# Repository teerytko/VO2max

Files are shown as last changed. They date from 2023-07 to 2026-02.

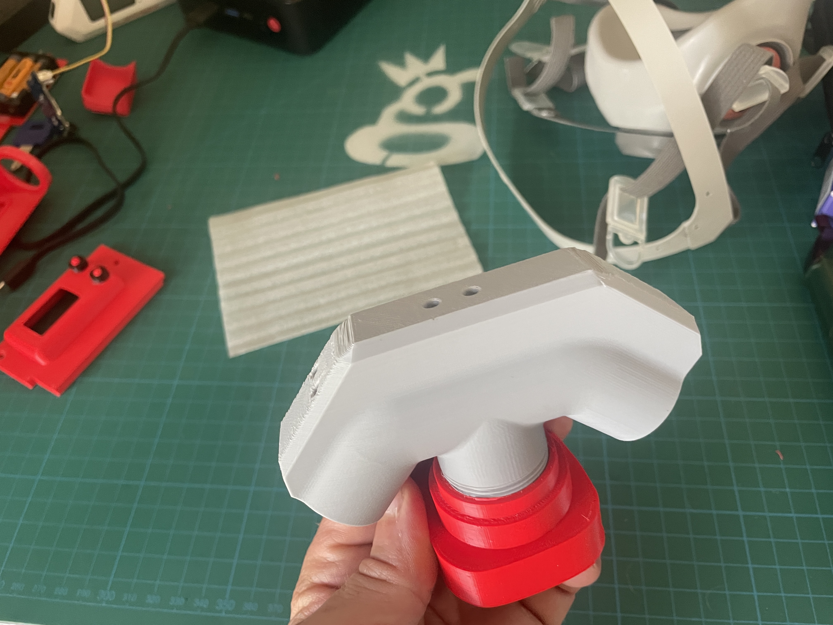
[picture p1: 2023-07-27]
images/first_print_v4_test.jpg

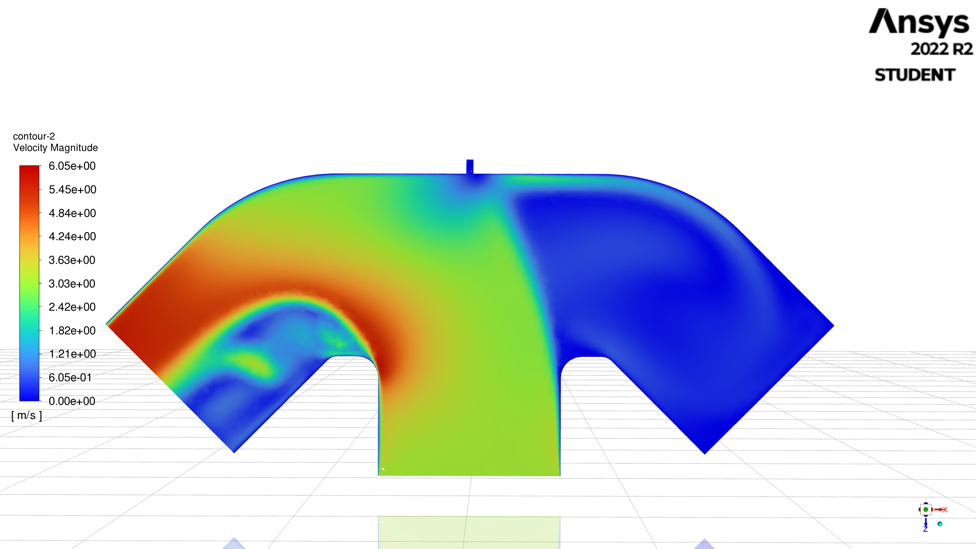
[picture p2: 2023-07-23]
images/flipped_CFD_results_w_velocity_contours.png

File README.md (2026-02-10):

# VO2 Max Mask 
Super cool project to build your own VO2 Max mask.  Your "VO2 Max" is a measure of how much oxygen your body and absorb and use during exercise, read more about it [here](https://www.healthline.com/health/vo2-max#benefits).

Original idea and detailed build instructions can be found on [Instructable](https://www.instructables.com/Accurate-VO2-Max-for-Zwift-and-Strava/). Other designs can be found [here, a UC Davis Med Center project](https://faculty.engineering.ucdavis.edu/knoesen/wp-content/uploads/sites/119/2016/12/OOCOO_WirelessHealthSubmission_Final.pdf) and a [commercial version that costs just under US$6,000](https://vo2master.com/).

This fork of [excellent Github work](https://github.com/meteoscientific/VO2max) incorporates the CO2 enhancements. The intent with this repo is to make it as easy as possible to build a world class piece of kit that'll add useful metrics to your training.

## Design Constraints
Less than $200 for all parts and printing.
Printable by anyone with a 3D printer (easy print files).
Can handle up to 200 liters per minute of exhaled air.
Small and light enough to be worn for a full workout.
Able to measure resting as well maximum VO2.

## App Intent
Allows an athlete to monitor real time [RER](https://www.adinstruments.com/signal/rer#:~:text=Respiratory%20Exchange%20Ratio%20(RER)%20is,is%20operating%20aerobically%20or%20anaerobically.).

Allows an athlete to monitor gross mechanical efficiency

The main mini version now aims to do just the basic VO2, VCO2 measurements, which can be sent via BLE to external device (e.g. phone). Any other sensors should connected to the phone as a data collection device.

## Versions
- V1 - Original version that works, can be found via the Instructable link above.
- V2 - Upgraded version by Urissel & Ivor, includes the CO2 & ambient temp/pressure to adapt to different elevation & temperatures.
- V3 - Proposed by Mahmoud, this is the T version.  Currently abandoned due to issues with getting correct sensor readings.
- V4 - Proposed by Stefan, affectionately called "The Snork".  Latest version.
- V5 - My latest version is based of V1, but not yet finalized. 

## Recent Firmware Status (as of 2026-02-08)
Latest commits in this repo:
- `f149ecc` (2026-02-08): Update the JSON outputs and scripts to match.
- `c29ee34` (2026-02-07): Add support for scripts parsing serial outputs.
- `f1a9a76` (2026-02-07): Refactor VO2 BLE server and serial output.
- `85bd076` (2026-02-07): Split BLE data into separate characteristics.
- `75d0030` (2026-01-06): Refactor volume calculations.

The active PlatformIO firmware lives in `TTGO_PlatformIo` and includes:
- `src/main.cpp`: Full firmware variant.
- `src/main_mini.cpp`: Newer "mini" variant with JSON serial telemetry and BLE service split.
- `src/vo2_ble_service.h` and `src/vo2_ble_service.cpp`: BLE server wrapper with separate characteristics for VO2, VCO2, and RQ.
- `tools/`: Python utilities for parsing and plotting serial JSON output.

### Steps to Build & Use
Check the build notes in `TTGO_PlatformIo/README`.

## Order Sensors, board, and assorted fasteners.
Check the [BOM](https://github.com/meteoscientific/VO2max/blob/main/BOM.md) for all the various parts to order, they can take a week or two to come in.

## Print 3D Parts
Print out the 3D parts using PLA.  This is still a work in progress, but feel free to explore the 3D Test Print directory and print out what you'd like.  Nothing works well yet (Aug 4th, 2023).

<br>Test fit all parts and make sure you know where everything goes; that will make the next steps much easier.

## Program Board
Originally this project was built with the Arduino IDE.  A few of us nerds decided that Platformio might be easier and more rad, so we're using that.

When you first get the board, hold down the boot button while plugging it in, and keep that down.  You need to erase everything on the board before you load the rest.  From there, you should be able to use the Platformio folder to load everything you'll need.  I did this on a Windows computer (a little Beelink with a monitor & display) because I couldn't get it to work on my Mac.

Current PlatformIO commands (from `TTGO_PlatformIo`):

```bash
platformio.exe run -e lilygo-vo2mini
platformio.exe run --target upload -e lilygo-vo2mini
platformio.exe test -e lilygo-vo2mini
platformio.exe device monitor -e lilygo-vo2mini
```

## Serial Output Tooling (JSON)
The `TTGO_PlatformIo/tools` directory now contains utilities for processing JSON serial output from the firmware:
- `serial_file_parser.py`: Parse JSON-lines from serial (`--port`) or from a captured file (`--file`).
- `live_visualize_serial.py`: Live plot JSON events from a serial port.
- `visualize_output.py`: Aggregate captured JSON-lines and generate HTML/PNG plots.

Install requirements and run examples:

```bash
python -m pip install -r TTGO_PlatformIo/tools/requirements.txt
python TTGO_PlatformIo/tools/serial_file_parser.py --port COM6 --baud 115200 --out-file output.json
python TTGO_PlatformIo/tools/visualize_output.py --input output.json --out-html output_plots.html --out-dir output_plots
```

## Wire It Up

## Assembly

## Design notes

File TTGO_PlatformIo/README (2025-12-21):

# Lilygo-T-Display VO2Max

# build (cmd line)
platformio.exe run -e lilygo-vo2mini

# build and upload (cmd line)
platformio.exe run --target upload -e lilygo-vo2mini

# test
platformio.exe test -e lilygo-vo2mini

# monitor / debug prints
platformio.exe device monitor -e lilygo-vo2mini

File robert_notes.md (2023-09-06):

Robert found this project and had the following notes, all relevant to the v1 form factor (not the v4 "Snork" designed by Stefan).

## Oxygen sensor:
1. As we know there is (or was) the issue of condensing air. In the new design it shouldn't be an issue anymore, if I'm correct? 
Anyway, I don't know which sensors the expensive spirometers use (do you?), but I'm guessing it's an oxygen sensor from the medical field.

Here's a [list of City Techs/Honeywell oxygen sensors](https://euro-gasman.com/app/uploads/2020/11/CITY-TECH-OXYGEN-SENSORS-LIST.pdf). Take a closer look at the "MediceL" ones: they are typically used for medical applications. 

The "best" as in "fastest response time" is the [MOX20](https://euro-gasman.com/app/uploads/2020/11/O2-MOX-20-MEDICEL-V2.pdf). It has a response time of <0.75s. That's quite fast, isn't it? If I remember correctly the data shouldn't be polled more often than once per second. Of course, being the fastest sensor comes at a high price (>$200).

What I noticed is that none of these sensors should be operated in condesing air. Even the MOX20 also states "Operating Humidity Range: 0-99% RH non-condensing". I haven't found a suitable sensor (T90 <5s) which works in a condensing environment. This leads me to believe that this can only be solved by design meaning we need to have a design which reduces condensate to a minimum.

Expensive spirometers will most likely use a sensor which won't work well in condensing air.

2. Response time: What is the response time of sensors used in expensive spirometers? I'm honestly guessing they are slower than 5s. Probably in the range of 5-15s. Which really is not that much of an issue for most of the time and as we are building a similar device we need to think about the importance of a fast response time. A faster than usual response time may even produce higher VO2max values than what the athlete might expect (I'll share more about that in the section "Calculations").

3. What I think we need is a cheap, fast enough, very reliable and if possible as long lasting oxygen sensor as possible. These sensors have pretty much an expiration date from the moment you first get them. Using a sensor with a high stability should be preferred.

4. I don't have a recommendation yet as I haven't really tested my VO2max mask enough. I read that some people complain about wrong readings, but I can't confirm that. If it works well the sensor should be suitable.

## CO2 sensor:
1. The SCD30's measurement range is not suited for accurately measuring our exhaled CO2 concentration. The range is 0-40,000 ppm which equals 0-4 vol%. As far as I know the exhaled CO2 concentration is always around the 4% mark (and my own tests confirm that). This makes the sensor inaccurate. 

2. Response time: The SCD30 has a pretty high response time of 20s to τ63%. Contrary to what I first thought this might not be that much of an issue, because we really only need CO2 for aerobic work measurements meaning at a VO2 below the maximum (depends on the athlete and the range should be from 60% VO2max to up to 90%). The reason is that the RQ should be at or higher than 1.0 as soon as the fat oxidation stops. This typically happens at your MaxLaSS (maximum lactate steady state, which is not the same but similiar to the FTP in biking). Below that threshold it doesn't really matter if it takes a minute to output the correct value, except for in-depth training analysis of high intensity workouts.

3. Keeping that in mind I'd say that having a low response time (<10s) is just an optional feature. Of course it shouldn't take much longer than the current SCD30 is able to accurately determine the CO2 concentration. The plus side is that CO2 sensors don't really come with an expiry date or it's as high as >10 years, so that's of no concern for us.

4. Recommendation? Well, again that's hard. I've searched but haven't really found the most suitable sensor for our device. There are some automotive sensors but I honestly forgot why I thought they aren't a good fit. Another sensor from Sensirion that uses a completely different technology than NDIR (SCD30) is the STC31, which uses a thermal conductivity measurement principle. Let me tell you the advantages first: it can measure a CO2 concentration of 0-25 vol% (or 0-250,000 ppm).

We'd only really need 0-5 vol%, but that's okay. It has an extremely fast measurement time of 66 ms, although I don't know how that value compares to the SCD30 as it says "measurement time" and not "τ63%". It works up to a humidity of 40°C dew point and does not seem to have issues with condensing air (the SCD30 does!). 40°C dew point is just a bit more than we need. It's extremely small. However, on the downside the accuracy of 0.5 vol% + 3% measured value might be too low and the small form factor makes it pretty much impossible to solder manually, but there are options available.
What do you think?

## Pressure sensor:
I haven't taken a look at this sensor. But I always wondered why we don't use something like the Sensirion SFM3400-AW (https://www.mouser.com/datasheet/2/682/Sensirion_Datasheet_SFM3400_AW_SFM3400_D-3002584.pdf)? Is it the price? This would eliminate the need to calibrate the sensor with a 3l calibration syringe.

## Ambient pressure sensor:
The current one seems to be okay, although the first one I got didn't work. Maybe my soldering skills were that bad and destroyed it but I think Nik (or someone else) had the same problem. Sounds to me that they aren't that reliable?

## Air flow:
The original design definitely had issues due to outside airflow interfering with the measurements. Think about this: When you are doing a VO2max test you will most likely run a fan or an ac. The fan will push air exactly in the direction the mask is facing. During my tests without a fan I could see changes in the measured expiratory volume and ventilation frequency just by moving around a little. Using a fan or an ac completely made the results unreliable. 

The new design will most likely be less affected by this, but even then the CO2 sensor might produce wrong results as the CO2 concentration will drop by a lot. This will probably not happen during VO2max tests (remember CO2 is not really of concern when measuring the VO2max) due to high ventilation, but it can happen when you want to know the correct CO2 concentration which is when you are working aerobically.
So what I did is inserting a 3M exhalation valve (exactly the same blue one which is included in the 3M mask) in the front of the original design. This is a single part I just glued on for testing purposes.

## Calculations:
1. I honestly haven't checked each calculation but I'm relying on them to be accurate.  What I noticed is that the VO2max might be a bit too high. When I did my last test with an expensive spirometer the guy said that sometimes a "single breath can produce a higher VO2" which is why he doesn't use this value to determine the VO2max and instead uses the highest average of 30s or something like that. This should be checked.

2. The CO2 sensor accepts ambient pressure readings. I have implemented that in my version of the code as we have the BMP280 to provide that data.

## Code:
1. I have replaced the existing SCD30 library with another one as the CO2 sensor needs to be calibrated from time to time (and due to the pressure sensor addition). We are not using the automatic self calibration which normally should be used with SCD30. This automatic calibration assumes that in a given time the sensor will reach the atmospheric CO2 concentration at least once. Automatic self calibration takes at least many hours up to days, which is not suitable for our device. Instead I implemented a function to self calibrate the CO2 sensor by running it for at least 2 minutes in outside air. Then it'll calibrate to 421 ppm which is the current atmospheric CO2 concentration of 2023. Remember, due to increasing CO2 in the air the value will increase each year and therefore using a value of 400 ppm would already create an error of 5% during calibration (not something we want in an accurate device). 2 minutes might not be enough but this step can be repeated or I can increase the timer in the code.

2. For my own tests I've changed some of the BLE code. In the future I would like to output all useful data to an app similar to a bike computer. The implementation can be done on the bluetooth level by sending each value as a specific service. This can then be combined with powermeter data, heart rate data and so on and even be saved in a FIT file or something like that.

There is an amazing website for analyzing of these files (www.intervals.icu) and the developer is a great guy who always listens to new ideas and often implements them (quite quick actually!).
The app itself is a work in progress and just something I would use but I can share it if it'll ever be ready.

5. The user interface could use an overhaul. My idea is to create multiple sections on the initial screen to make it more clear (Start, Settings, Status) and by using submenus to navigate further.

6. The code has quite a lot of comments (thanks for that) which make it easy to understand. Still it could be reorganized a little. But that's not really important now.

I've probably forgot some points but I'll share them if I remember.
Let me know your thoughts.

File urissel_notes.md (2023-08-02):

*I found the notes from Ulli Rissel in Rabbitcreek's updates hard to read as one giant paragraph, so I've broken them down a bit here, cut some parts out that related to the original venture tube design, and added in a few of Ulli's notes.*

## Upgrades from original:

  1. I added a barometric sensor (BMP180) to calculate the air density. The calculation of VO2 should also be correct in the mountains thanks to the barometric sensor. The BMP180 sensor is connected to the I2C bus like the other sensors. I glued it between the two sensors on the Venturi tube. In Arduino, the library "Adafruit_BMP085" must be added.

  2. The VO2max and VEmin calculation is carried out with moving averages and measurement of each individual breath. This allows current measured values every 5 seconds. 

  3. The displays of the values can be switched during the measurement.

  4. If the sensor reaches its limit (at approx. 4.5L/s corresponding to a VEmin of 136L/min!) this is displayed. However, the error should only be minimal. If the limit is displayed too often, the Venturi nozzle would have to be modified. 

  5. A warning appears if the O2 sensor measures less than 20% VO2% at startup. Then the sensor (or room) needs to be ventilated before moving on. If "Continue" is pressed anyway, the value is set to 20.9%.

  6. Battery indicator: The voltage is displayed with background color to the state of charge. White: USB or charge, Green: Battery full, Yellow: Battery approx. 50%, Red: Battery approx. 20%. The display takes place at the top left. A 1100mAh Lipo lasts about 10h!

  7. Kcal are now calculated correctly with their own integral timer.

  8. DEMO mode when the top button is pressed when powered on. It simulates about 28L of respiratory minute volume with respiratory rate of 12 at 4% CO2. This allows you to test the data transfer.

  9. Reset by pressing both buttons. This works after the 3L check.

  10. The volume measurement was measured with a 3L calibration pump and a calibration factor was programmed. The volume measurement can be checked in the first 10 seconds with a real-time display. I tested 2 sensors and for practical reasons set the average calibration factor 0.92 for volume measurement. 

You are welcome to customize this in the program itself (is easy to find).

  11. The data is sent every 5 seconds as csv via USB cable and Bluetooth serial. Data transmission with cable and BT starts immediately after "Press to start". With Excel Datastream, a display can be made in real time.BT on Excel works really well, even with instant graphical representation. 

You can also send the data to the APP Bluetooth Serial Monitor on an Android mobile phone and process or send it from there.

### Some thoughts on the calculation: 

The common spirometers measure the inspiration volume Vi in the supply line, not Ve. 

However, the concentration of O2 and CO2 is measured **expiratory**. 

Therefore, Ve must be calculated in order to correctly record the O2 consumption. 

Three factors come into play: 
  1) The volume shrinks minimally if less CO2 is produced than O2 is absorbed (i.e. at quotient <1). This can be corrected via the Haldane formula. However, the deviations are minimal. 
  2) Much more important is that BTPS conditions prevail in the expiration air (35°C, 95% humidity, actual ambient pressure). 
  3) The measurement has to be converted to STPD conditions (0 °C, 1013.25 hPa, 0% humidity). 

VO2 is defined under STPD conditions. STPD stands for standard temperature (0°C or 273 K) and pressure (760 mm Hg) and dry (no water vapor). 

According to my research, the conversion is nothing more than the ratio of the density of BTPS (actually measured pressure, 37°C, 95% humidity) to STPD. 

*The two symbols BTPS and STPD represent two conventional conditions used when discussing respiratory gases. BTPS stands for body temperature (37°C), ambient pressure and gas saturated with water vapor, whereas STPD stands for standard temperature (0°C or 273 K) and pressure (760 mm Hg) and dry (no water vapor). Pulmonary ventilation (1/min) is usually measured at BTPS, whereas gas volumes in blood are usually expressed at STPD. To convert a gas volume at BTPS to one at STPD, one needs to multiply the former volume by (273/310) (PB − 47) / 760.* [National Library of Medicine reference](https://www.ncbi.nlm.nih.gov/books/NBK54114/)

The density of STPD is constant = 1.2922 kg/m³. The density of BTPS can be easily calculated, whereby instead of the gas constant 287.058, the constant for moist air is used for BTPS (about 292.8). 

The constant fluctuates in our temperature range depending on pressure only by a few percent, the density only in the per mille range, if 292.8 is not adjusted. The density indicates how many molecules are in the air.  And now it becomes relatively simple: We measure Ve directly, so no further conversion is required. 

This results in: VO2 = Ve * O2diff% * Density BTPS / 1.2922. Done! By the way, according to the spirometry instructions, VO2 is only calculated from the O2 difference. 

The density must be related to the density under standard conditions. This means that rho must be divided by 1,225. All values are then about 20% lower:

co2 = initialO2 - lastO2; //calculated level of CO2 based on Oxygen level loss
if (co2 < 0) co2 = 0; // correction for sensor drift
vo2Total = volumeVEmean * (rho/1.225) * co2 * 10; // = vo2 in ml/min (* co2% * 10 for L in ml)
vo2Max = vo2Total / weightkg; //correction for wt

VO2Total and vo2Max in ml/min/kg
volumeVEmean: breath volume in L/min. (running mean)
rho: density of the air in kg/m³

CO2 is only used to calculate the quotient and for the Haldane formula, which we do not need.

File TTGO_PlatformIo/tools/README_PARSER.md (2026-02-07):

Serial/File Parser

This repository includes a small Python utility that reads lines from either a text file or a serial port and prints parsed output.

Files:
- [scripts/serial_file_parser.py](scripts/serial_file_parser.py)
- [requirements.txt](requirements.txt)

Install dependencies:

```bash
python -m pip install -r requirements.txt
```

Examples:

Read a file:

```bash
python scripts/serial_file_parser.py --file data.txt
```

Read from a serial port (Windows example):

```bash
python scripts/serial_file_parser.py --port COM6 --baud 115200
```

Options:
- `--raw`: print raw lines (or JSON records if lines are JSON)
- `--limit N`: stop after N lines

Behavior:
- Each input line is first attempted to be parsed as JSON; if parsing fails the line is returned as raw text.

Visualization:

- A visualization utility is available at `scripts/visualize_output.py` that reads a JSON-lines file (like `output.json`), aggregates measurements per "expiration" event and creates interactive and static plots.

Examples:

```bash
python scripts/visualize_output.py --input output.json --out-html output_plots.html --out-dir output_plots
```

This will create `output_plots.html` (interactive Plotly charts) and PNG files in the `output_plots` directory.

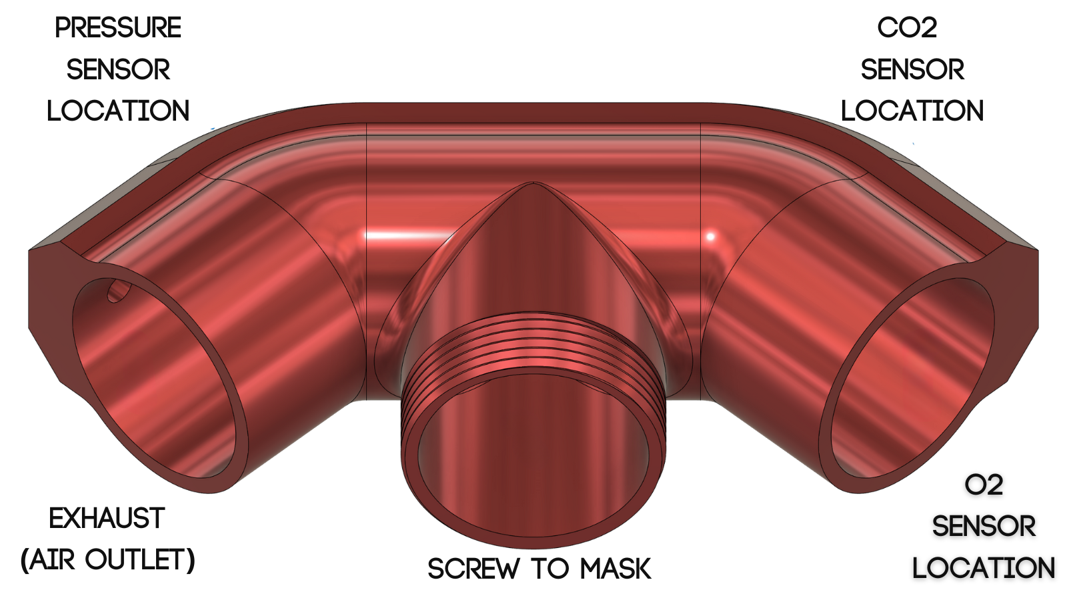
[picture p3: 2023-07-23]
images/redesign_of_VO2_Max_housing.png

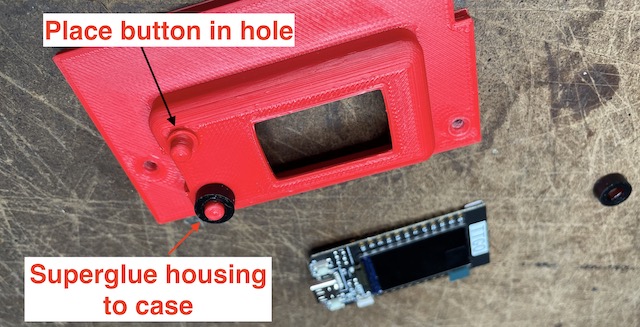
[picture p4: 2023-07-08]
images/button_housing.jpg

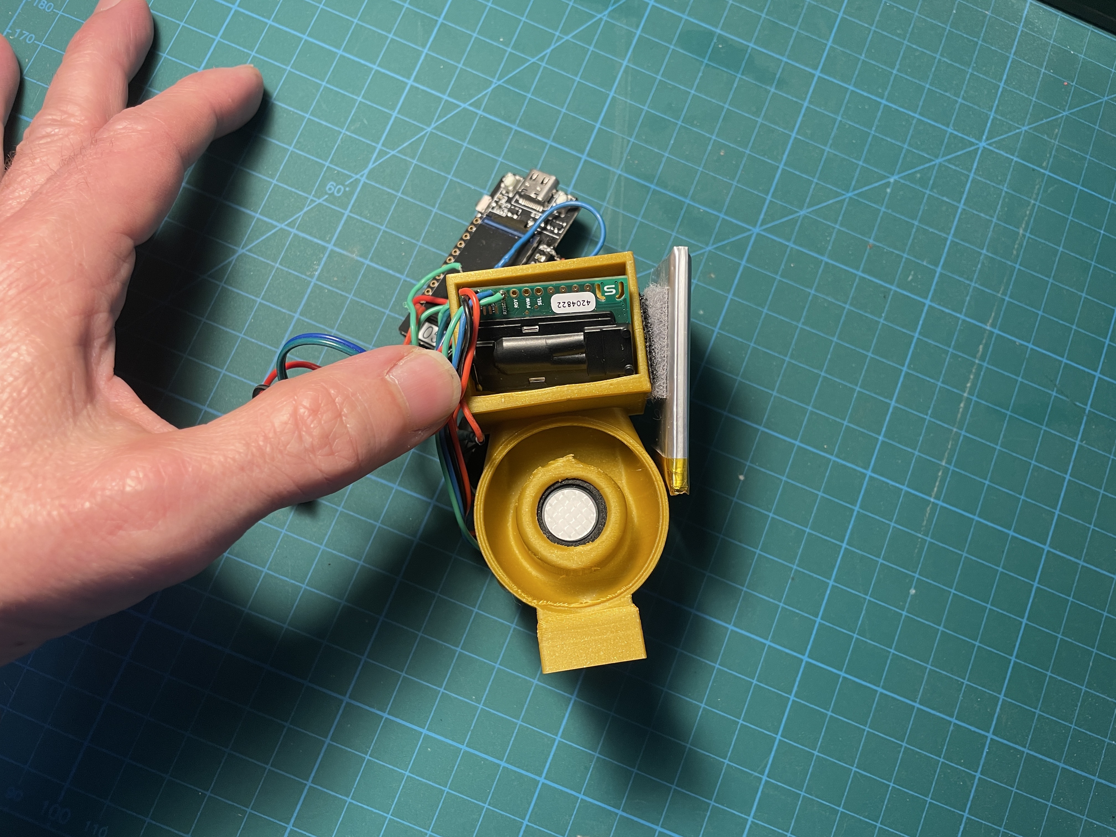
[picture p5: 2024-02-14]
images/v4_snork/vo2_inside.JPG

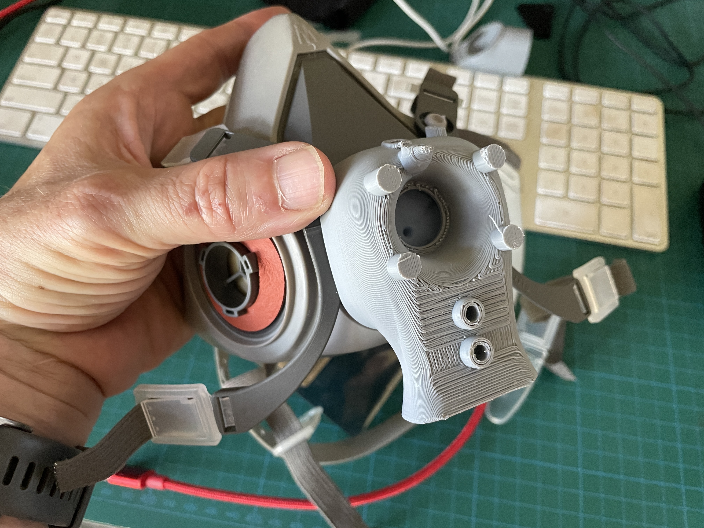
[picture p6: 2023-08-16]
images/v4_snork/v4_snork_1.jpg

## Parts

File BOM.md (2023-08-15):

## Bill of Materials

### USA

| Item | Description/Details | Source | Est Cost |
| --- | --- | --- | --- |
| board (the brain) | ESP32 T-Display, 16MB CH9102F | [Amazon](https://www.amazon.com/gp/product/B099MPFJ9M/) | $19 |
| battery| Lipo Battery, 1000 Mah, E503450 3.7v |  [Amazon](https://www.amazon.com/gp/product/B07BTV3W87/ref=ox_sc_act_title_1?smid=A132D7PL1YID8X&psc=1) | $12 |
| pressure sensor | BMP280, calculate air density |  [Amazon](https://www.amazon.com/gp/product/B01ICN5QPU/ref=ox_sc_act_title_1?smid=A30QSGOJR8LMXA&psc=1) | $6 |
| screws | 2 x M3 x 8mm | [Amazon](https://www.amazon.com/Hilitchi-510-Pcs-Button-Socket-Assortment/dp/B073SWNV5N/) | $15 for kit |
| threaded inserts (original design only) | M3 x 8 x 5mm | [Amazon](https://www.amazon.com/gp/product/B096MD67WB/) | $18 for kit |
| aquarium tubing (original design only) | standard 3/16", 4mm inside diameter (ID) |  [Amazon](https://www.amazon.com/AQUANEAT-Standard-Airline-Aquarium-PREMIUM/dp/B01N8SNNOI/) | $6 |
| o-ring | for oxygen sensor, 22x19x1.5mm | [Amazon](https://www.amazon.com/uxcell-Silicone-Rings-Diameter-Gasket/dp/B082STZ4XL?th=1) | $7 for 30 |
| jumper wire | for making board-sensor connections | [Amazon](https://www.amazon.com/TUOFENG-Hookup-Wires-6-Different-Colored/dp/B07TX6BX47?th=1) | $15 |
| oxygen sensor | Gravity: I2C Oxygen Sensor |  [DF Robot](https://www.dfrobot.com/product-2052.html) | $75 |
| differential pressure sensor | Omron--D6F-PH0025AD2 |  [Digikey](https://www.digikey.com/en/products/detail/omron-electronics-inc-emc-div/d6f-ph0025amd2/15197363) | $28 |
| cable for diff press sensor | DF-CABLE3 |  [Digikey](https://www.digikey.com/en/products/detail/omron-electronics-inc-emc-div/D6F-CABLE3/9471785) | $12 |
| mask | half mask, particulate matter, 6200/07025 | [Digikey](https://www.digikey.com/en/products/detail/3m/6200-07025/7693860) | $22 |
| CO2 sensor | SCD30 |  [Digikey](https://www.digikey.com/en/products/detail/sensirion-ag/SCD30/8445334) | $62 |
| on/off switch | mini push button |  [Adafruit](https://www.adafruit.com/product/1683)| $6 |

### EU

| Item | Description/Details | Source | Est Cost (€) |
| --- | --- | --- | --- |
| board (the brain) | ESP32 T-Display, 16MB CH9102F | [Amazon](https://www.amazon.de/-/en/gp/product/B099MPFJ9M) | €23 |
| battery| Lipo Battery, 1000 Mah, E503450 3.7v |  [Amazon](https://www.amazon.de/-/en/gp/product/B09GK98KZK) | €18 |
| pressure sensor | BMP280, calculate air density |  [Amazon](https://www.amazon.de/-/en/gp/product/B0BN1NXG4D) | €6 for 5 |
| screws | 2 x M3 x 8mm | [Amazon](https://www.amazon.de/-/en/340pcs-Stainless-Screws-Button-Assortment/dp/B08H24T1DJ) | €9 for kit |
| threaded inserts (original design only) | M3 x 8 x 5mm | [Amazon](amazon.de/gp/product/B09ZHSGHXD) | tbd |
| aquarium tubing (original design only) | standard 3/16", 4mm inside diameter (ID) | [eBay](http://ebay.de/itm/183220505584?var=691579886173) | tbd |
| o-ring | for oxygen sensor, 22x19x1.5mm | [Amazon](https://www.amazon.de/-/en/gp/product/B00AKW4MM0) | €5 for 10 |
| jumper wire | for making board-sensor connections | [eBay1](ebay.de/itm/184844268251) [eBay2](ebay.de/itm/184844268251) | tbd |
| oxygen sensor | Gravity: I2C Oxygen Sensor |  [Mouser](https://eu.mouser.com/ProductDetail/426-SEN0322) | €49 |
| differential pressure sensor | Omron--D6F-PH0025AD2 |  [Mouser](https://eu.mouser.com/ProductDetail/653-D6F-PH0025AD2) | €26 |
| cable for diff press sensor | DF-CABLE3 |  tbd | tbd |
| mask | half mask, particulate matter, 6200/07025 | [Amazon](https://www.amazon.de/-/en/gp/product/B005HK05L2) | €21 |
| CO2 sensor | SCD30 |  [Amazon](https://www.amazon.de/-/en/gp/product/B0B9MYCL3S) or [Watterott](http://shop.watterott.com/Sensirion-SCD30-CO2-Kohlendioxid-Sensor) | €43 |
| on/off switch | mini push button |  [Mouser](https://eu.mouser.com/ProductDetail/Adafruit/1683)| €2 |

Prices are rounded and exclude VAT.

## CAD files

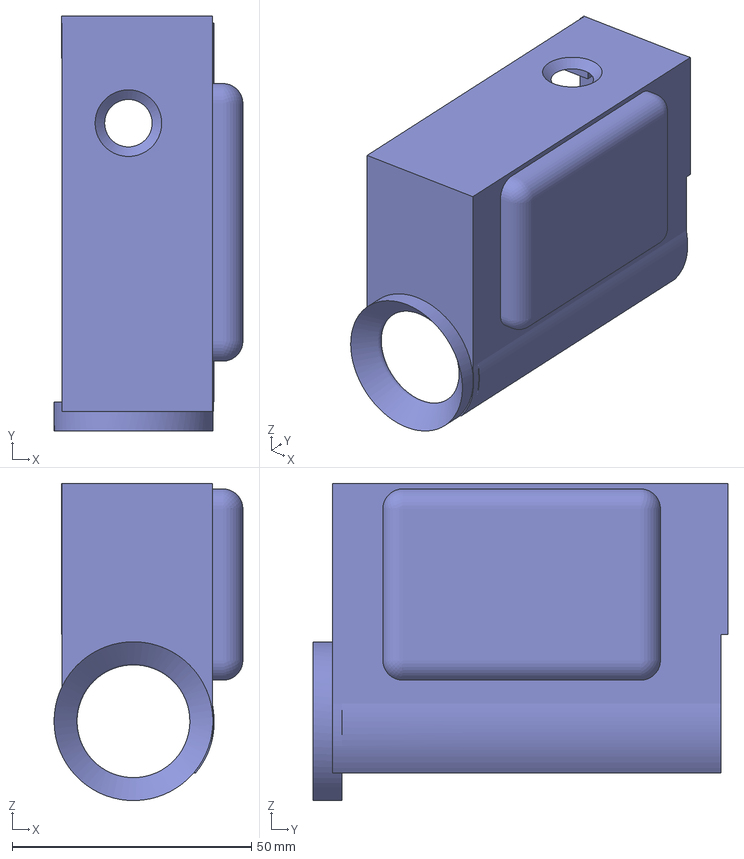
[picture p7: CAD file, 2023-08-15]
3d-print-files/v1/MainBody.3mf
39.5 x 86.8 x 66.3 mm

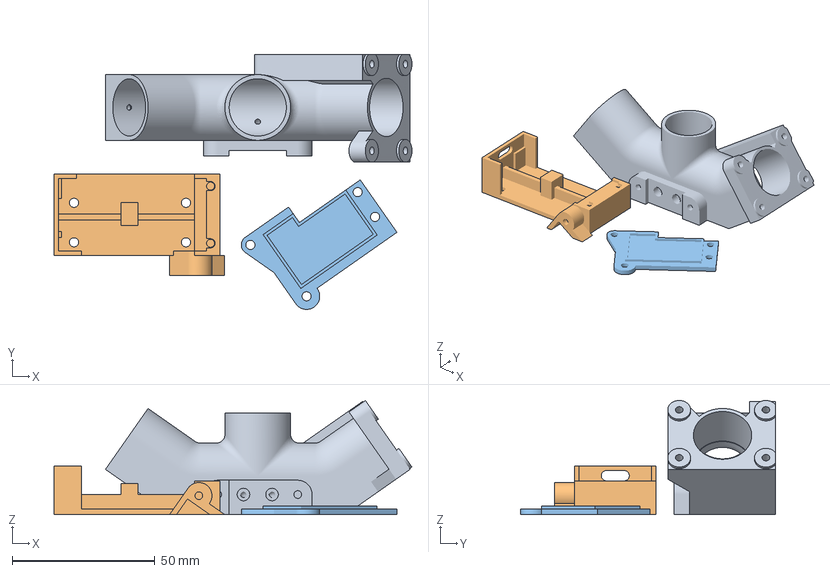
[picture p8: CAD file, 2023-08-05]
3d-print-files/T0 230802 VO2 Max v1_1.3mf
125.3 x 89.2 x 39.9 mm
230802 VO2 Max v1_1
230802 VO2 Max v1_2
230802 VO2 Max v1_3

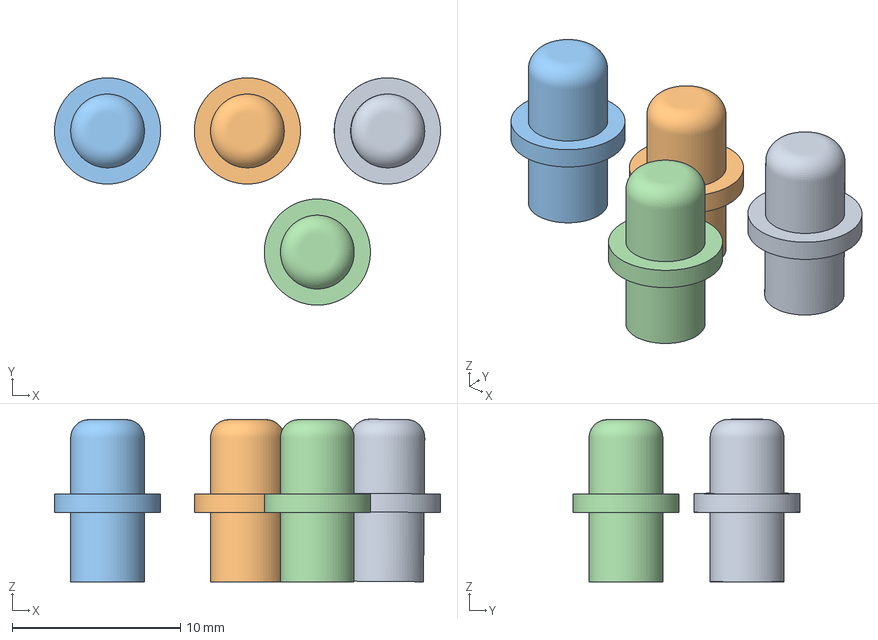
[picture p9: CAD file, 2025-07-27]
3d-print-files/v1/button.3mf
22.9 x 13.5 x 9.66 mm

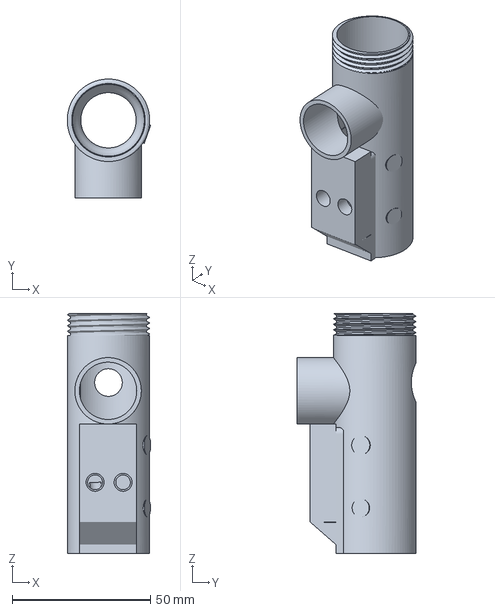
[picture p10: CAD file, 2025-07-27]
3d-print-files/v1/CO2_upgrade/Venturi CO2 20mm.3mf
30.2 x 43.0 x 86.8 mm

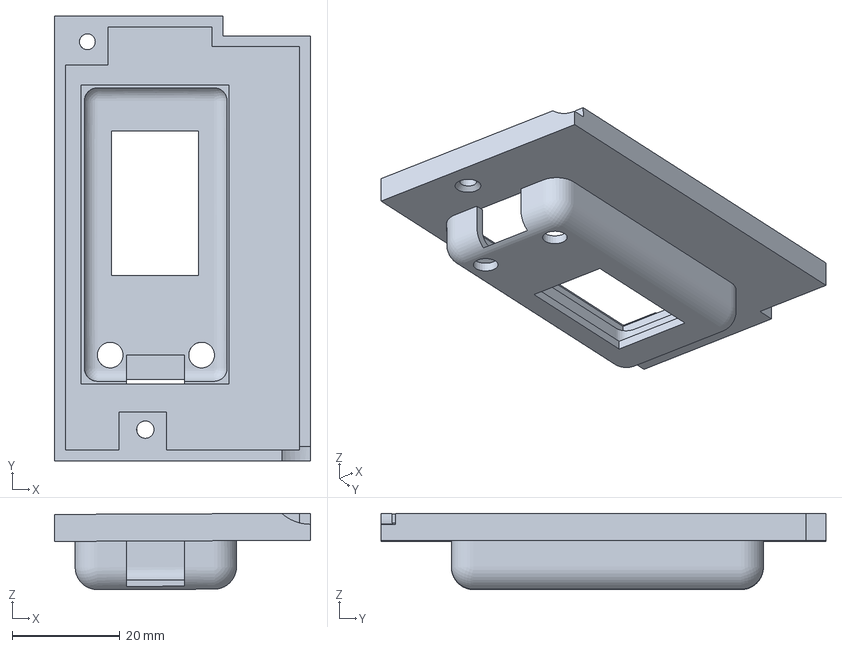
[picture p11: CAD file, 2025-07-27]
3d-print-files/v1/SideComputer.3mf
47.6 x 82.6 x 14.2 mm

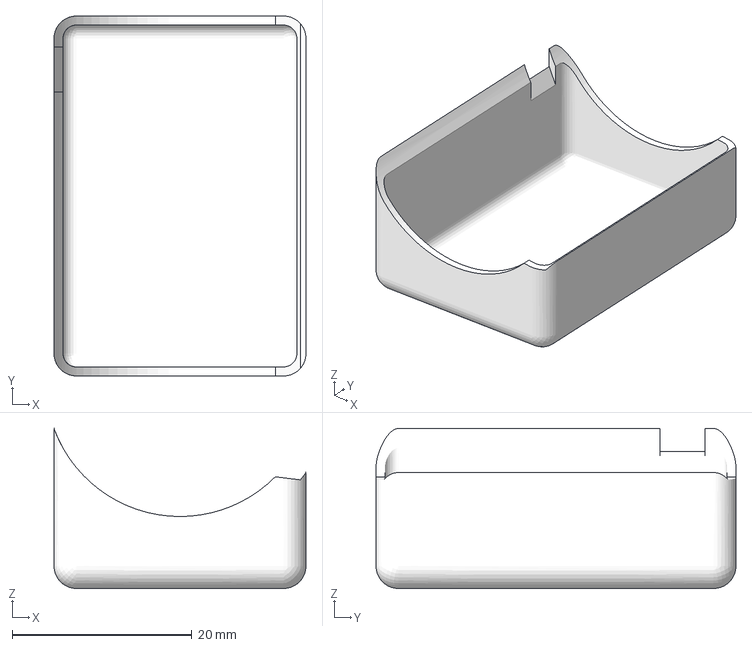
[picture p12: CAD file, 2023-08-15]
3d-print-files/v1/CO2_upgrade/SCD30 Cover.3mf
28.0 x 40.0 x 17.8 mm

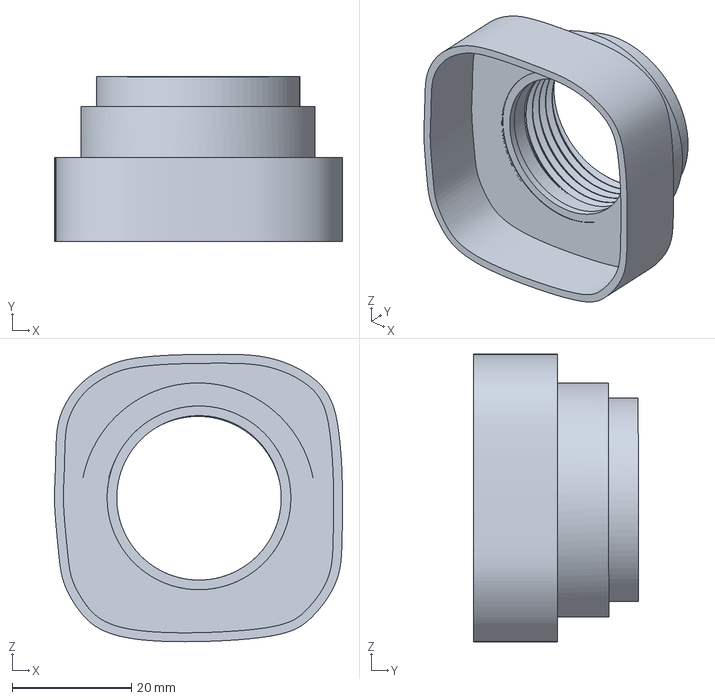
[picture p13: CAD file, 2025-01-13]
3d-print-files/v1/MaskAttachment.3mf
48.2 x 27.7 x 48.2 mm

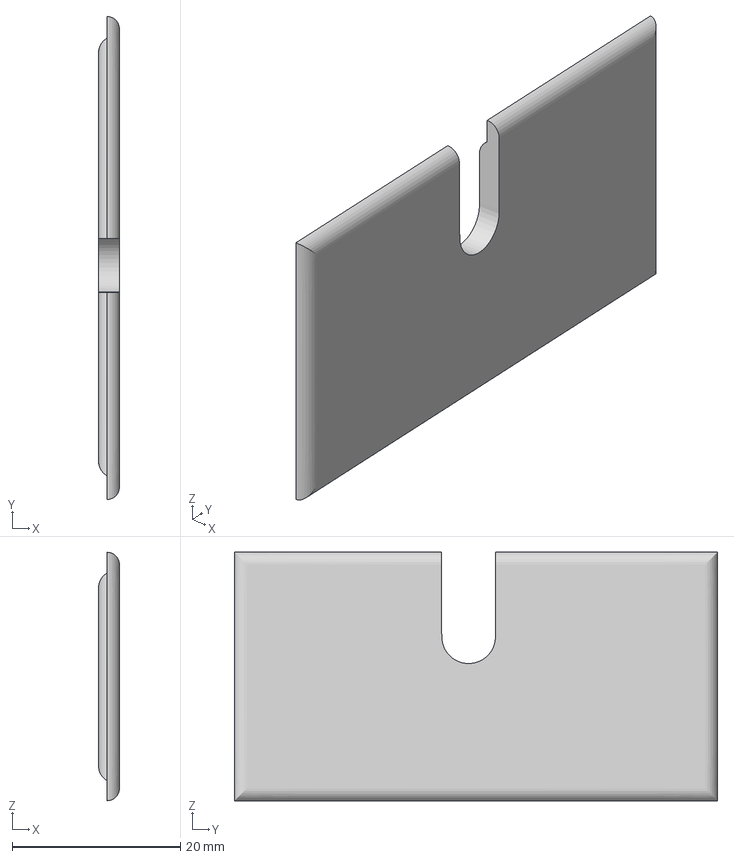
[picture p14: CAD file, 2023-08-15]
3d-print-files/v1/ComputerCover.3mf
2.49 x 57.5 x 29.6 mm

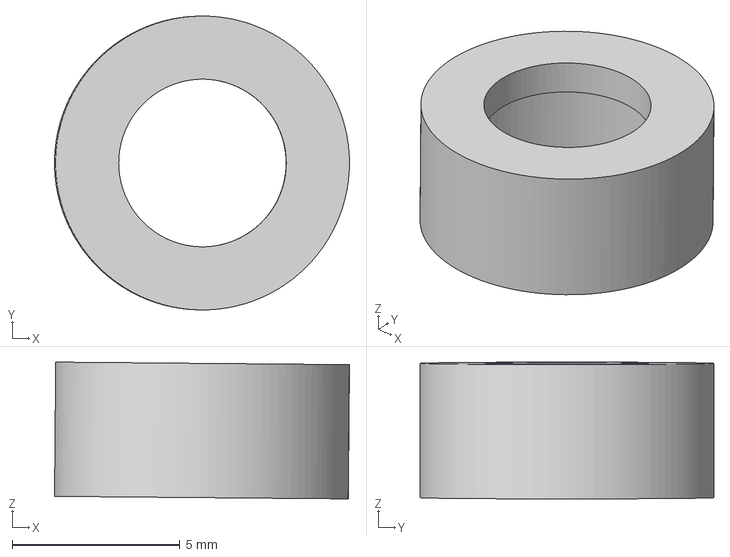
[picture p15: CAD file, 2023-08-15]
3d-print-files/v1/buttonHousing.3mf
8.79 x 8.75 x 4.08 mm

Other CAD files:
3d-print-files/v1/CO2_upgrade/Venturi CO2 16mm.3mf
3d-print-files/v1/VenturiSensor.3mf

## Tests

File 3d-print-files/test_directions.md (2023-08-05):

## Test 3D Print Files

At the end of this project none of these will be what you'll use, but in the meantime you may find this useful.  Feel free to print these out or take a look and make any suggestions.

There will be multiple files in here, pay close attention to the file names (T0 vs T1 etc).

STEP files are in the zip folders if you want to get jiggy with 'em.

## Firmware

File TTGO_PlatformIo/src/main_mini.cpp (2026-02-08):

//+++++++++++++++++++++++++++++++++++++++++++++++++++++++++++++++
// Mini version
//
// TTGO T-Display: SDA-Pin21, SCL-Pin22
//+++++++++++++++++++++++++++++++++++++++++++++++++++++++++++++++

/*Board: ESP32 Dev Module
Upload Speed: 921600
CPU Frequency: 240Mhz (WiFi/BT)
Flash Frequency: 80Mhz
Flash Mode: QIO
Flash Size: 4MB (32Mb)
Partition Scheme: Default 4MB with spiffs (1.2MB APP/1.5 SPIFFS)
Core Debug Level: None
PSRAM: Disabled*/

// Set this to the correct printed case venturi diameter
#define DIAMETER 18

#undef VERBOSE // additional debug logging

#include <Arduino.h>
#include "esp_adc_cal.h" // ADC calibration data
#include <EEPROM.h>      // include library to read and write settings from flash
#define ADC_EN 14        // ADC_EN is the ADC detection enable port
#define ADC_PIN 34
int vref = 1100;

#include <SPI.h>
#include <TFT_eSPI.h> // Graphics and font library for ST7735 driver chip
#include <Wire.h>
#include "DFRobot_OxygenSensor.h" //Library for Oxygen sensor
#include "SCD30.h"                //Library for CO2 sensor
#include "Omron_D6FPH.h"          //Library for differential pressure sensor
#include "vo2_ble_service.h"          //Library for differential pressure sensor

// Starts Screen for TTGO device
TFT_eSPI tft = TFT_eSPI(); // Invoke library, pins defined in User_Setup.h

// Labels the pressure sensor
Omron_D6FPH presSensor;

// Label of oxygen sensor
DFRobot_OxygenSensor Oxygen;
#define COLLECT_NUMBER 10           // collect number, the collection range is 1-100.
#define Oxygen_IICAddress ADDRESS_3 // I2C  label for o2 address
const String Version = "V2.3 2026/02/07";

// Defines button state for adding wt
const int buttonPin1 = 0;
const int buttonPin2 = 35;
int wtTotal = 0;
int buttonPushCounter1 = 0; // counter for the duration of button1 pressed
int buttonState1 = 1;       // current state of the button
int buttonPushCounter2 = 0; // counter for the duration of button2 pressed
int buttonState2 = 1;       // current state of the button
int screenChanged = 0;
int screenNr = 1;
int HeaderStreamed = 0;
int HeaderStreamedBT = 0;
int DEMO = 0; // 1 = DEMO-mode

// ############################################
//  Select correct diameter depending on printed
//  case dimensions:
// ############################################

// Defines the size of the Venturi openings for the  calculations of AirFlow
float area_1 = 0.000531; // = 26mm diameter
//float area_1 = 0.000401; // = 22,6mm diameter
#if (DIAMETER == 20)
float area_2 = 0.000314; // = 20mm diameter
#elif (DIAMETER == 19)
float area_2 = 0.000284; // = 19mm diameter
#elif (DIAMETER == 18)
float area_2 = 0.000254; // = 18mm diameter
#else // default
float area_2 = 0.000201; // = 16mm diameter
#endif

float rho = 1.225;     // ATP conditions: density based on ambient conditions, dry air
float rhoSTPD = 1.292; // STPD conditions: density at 0°C, MSL, 1013.25 hPa, dry air
float rhoBTPS = 1.123; // BTPS conditions: density at ambient  pressure, 35°C, 95% humidity
float massFlow = 0;
float volFlow = 0;
float volumeTotal = 0;      // variable for holding total volume of breath
float pressure = 0.0;       // differential pressure of the venturi nozzle
float pressThreshold = 0.1; // threshold for starting calculation of VE
float volumeVE = 0.0;
float volumeVEmean = 0.0;
float volumeExp = 0.0;

// ##############################################################################################

// Basic defaults in settings, saved to eeprom
struct
{
    int version = 1;              // Make sure saved data is right version
    float correctionSensor = 1.0; // calculated from 3L calibration syringe
    float weightkg = 80.0;        // Standard-body-weight
    bool co2_on = false;          // CO2 sensor active
    bool bmp_on = false;          // Pressure sensor sensor active
} settings;

float TimerInspiration = 0.0;
float TimerExpiration = 0.0;
float TimerVolCalc = 0.0;
float Timer5s = 0.0;
float Timer1min = 0.0;
float TimerVO2calc = 0.0;
float TimerVO2diff = 0.0; // used for integral of calories
float TimerStart = 0.0;
float TotalTime = 0.0;
String TotalTimeMin = String("00:00");
int readVE = 0;
float TimerVE = 0.0;
float DurationVE = 0.0;
float lastO2 = 0;
float initialO2 = 0;
float deltaO2_frac = 0;
float calTotal = 0;
float vo2Cal = 0;
float vo2CalH = 0;        // calories per hour
float vo2CalDay = 0.0;    // calories per day
float vo2CalDayMax = 0.0; // highest value of calories per day
float vo2Rel = 0;         // value of vo2rel ml/min/kg, calculated every 30 seconds
float vo2Total = 0.0;     // value of total vo2Max/min
float vo2MaxMax = 0;      // Best value of vo2 max for whole time machine is on
float respq = 0.0;      // respiratory quotient in mol VCO2 / mol VO2
float co2ppm = 0.0;     // CO2 sensor in ppm
float co2perc = 0.0;    // = CO2ppm /10000
float initialCO2 = 0.0; // initial value of CO2 in ppm
float calibCO2 = 0.0;   // The CO2 (ppm) value after the calibration process
float vco2Total = 0.0;
float vco2Rel = 0.0;
float co2temp = 0.0; // temperature CO2 sensor
float co2hum = 0.0;  // humidity CO2 sensor (not used in calculations)
float freqVE = 0.0;     // ventilation frequency
float freqVEmean = 0.0; // mean ventilation frequency
float expiratVol = 0.0; // last expiratory volume in L
float volumeTotalOld = 0.0;
float volumeTotal2 = 0.0;
float TempC = 15.0;    // Air temperature in Celsius barometric sensor BMP180
float PresPa = 101325; // uncorrected (absolute) barometric pressure
float Battery_Voltage = 0.0;
// if ble
VO2BleServer bleServer;

enum ventilationStates
{
    WAITING_PRESSURE,
    INSPIRATION,
    EXPIRATION,
    EXPIRATION_DONE
};

enum deviceStates
{
    DEVICE_INITIALIZE,
    DEVICE_READY,
    DEVICE_CALIBRATE,
    DEVICE_MEASURE
};

int ventilationState = WAITING_PRESSURE;
int state = DEVICE_INITIALIZE;
// Forward declarations
uint16_t readVoltage();     // read battery voltage
float readCO2();         // read CO2 sensor
float readO2();         // read CO2 sensor
float volumeCalc();         // (
void vo2maxCalc();
void CheckInitialCO2(); // check initial CO2 value
void CheckInitialO2();  // check initial O2 value
void showScreen(float o2, float co2, float respq, float vol);      // show screen on OLED
void ReadButtons();     // read buttons
void tftScreen1(float o2, float co2, float respq, float vol);      // show screen 1 on TFT
void tftParameters();   // show parameters on TFT
void GetWeightkg();     // get weight from scale

void loadSettings()
{
    // Check version first.
    int version = EEPROM.read(0);
    if (version == settings.version)
    {
        for (int i = 0; i < sizeof(settings); ++i)
            ((byte *)&settings)[i] = EEPROM.read(i);
    }
}

void saveSettings()
{
    bool changed = false;
    for (int i = 0; i < sizeof(settings); ++i)
    {
        byte b = EEPROM.read(i);
        if (b != ((byte *)&settings)[i])
        {
            EEPROM.write(i, ((byte *)&settings)[i]);
            changed = true;
        }
    }
    if (changed)
        EEPROM.commit();
}

//----------------------------
void setup()
{
    EEPROM.begin(sizeof(settings));

    pinMode(buttonPin1, INPUT_PULLUP);
    pinMode(buttonPin2, INPUT_PULLUP);

    // defines ADC characteristics for battery voltage
    /*
      ADC_EN is the ADC detection enable port
      If the USB port is used for power supply, it is turned on by default.
      If it is powered by battery, it needs to be set to high level
    */
    // setup for analog digital converter used for battery voltage ---------
    pinMode(ADC_EN, OUTPUT);
    digitalWrite(ADC_EN, HIGH);
    esp_adc_cal_characteristics_t adc_chars;
    esp_adc_cal_value_t val_type = esp_adc_cal_characterize(ADC_UNIT_1, ADC_ATTEN_DB_11, ADC_WIDTH_BIT_12, 1100, &adc_chars);
    // Check type of calibration value used to characterize ADC
    if (val_type == ESP_ADC_CAL_VAL_EFUSE_VREF)
    {
        Serial.printf("eFuse Vref:%u mV", adc_chars.vref);
        vref = adc_chars.vref;
    }
    else if (val_type == ESP_ADC_CAL_VAL_EFUSE_TP)
    {
        Serial.printf("Two Point --> coeff_a:%umV coeff_b:%umV\n", adc_chars.coeff_a, adc_chars.coeff_b);
    }
    else
    {
        // Serial.println("Default Vref: 1100mV");
    }

    // init display ----------
    tft.init();
    tft.setRotation(1);
    tft.fillScreen(TFT_BLACK);

    readVoltage();
    tft.setTextColor(TFT_WHITE, TFT_BLACK);
    tft.drawString("VO2max", 0, 25, 4);
    tft.drawString(Version, 0, 50, 4);
    tft.drawString("Initialising...", 0, 75, 4);
    // check for DEMO mode ---------
    if (!digitalRead(buttonPin2))
    { // DEMO Mode if button2 is pressed during power on
        DEMO = 1;
        tft.setTextColor(TFT_RED, TFT_BLACK);
        tft.drawString("DEMO-MODE!", 0, 100, 4);
    }
    delay(3000);
    tft.fillScreen(TFT_BLACK);

    // init serial communication  ----------
    Wire.begin();
    Serial.begin(115200); // drop to 9600 to see if improves reliability
    if (!Serial)
    {
        tft.drawString("Serial ERROR!", 0, 0, 4);
    }
    else
    {
        tft.drawString("Serial ok", 0, 0, 4);
    }
    
    // 
    if (bleServer.initialize())
    {
        tft.drawString("BLE init ok", 0, 25, 4);
    }
    else
    {
        tft.drawString("BLE init ERROR!", 0, 25, 4);
    }

    // init O2 sensor DF-Robot -----------
    if (!Oxygen.begin(Oxygen_IICAddress))
    {
        tft.drawString("O2 ERROR!", 0, 75, 4);
    }
    else
    {
        tft.drawString("O2 ok", 0, 75, 4);
    }

    // init CO2 sensor Sensirion SCD30 -------------
    // check if sensor is connected?
    scd30.initialize();
    scd30.setAutoSelfCalibration(0);
    while (!scd30.isAvailable())
    {
        tft.drawString("CO2init..", 120, 75, 4);
    }
    tft.drawString("CO2 ok", 120, 75, 4);

    CheckInitialO2();
    // Disable CO2 for now
    CheckInitialCO2();
    // init flow/pressure sensor Omron D6F-PF0025AD1 (or D6F-PF0025AD2) ----------
    while (!presSensor.begin(MODEL_0025AMD2))
    {
        // Serial.println("Flow sensor error!");
        tft.drawString("Flow-Sensor ERROR!", 0, 100, 4);
    }
    // Serial.println("Flow-Sensor I2c connect success!");
    tft.drawString("Flow-Sensor ok", 0, 100, 4);
    delay(2000);

    tft.fillScreen(TFT_BLACK);
    tft.setTextColor(TFT_GREEN, TFT_BLACK);

    tft.drawCentreString("Ready...", 120, 55, 4);
    state = DEVICE_READY;
    TimerVolCalc = millis(); // timer for the volume (VE) integral function
    Timer5s = millis();
    Timer1min = millis();
    TimerVO2calc = millis(); // timer between VO2max calculations
    TimerStart = millis();   // holds the millis at start
    TotalTime = 0;
    // BatteryBT(); // TEST for battery discharge log
    // ++++++++++++++++++++++++++++++++++++++++++++
}

//----------------------------------------------------------------------------------------------------------
//                  MAIN PROGRAM
//----------------------------------------------------------------------------------------------------------
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

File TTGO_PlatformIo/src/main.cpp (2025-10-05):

//+++++++++++++++++++++++++++++++++++++++++++++++++++++++++++++++
// Spirometrie Project
// https://www.instructables.com/Accurate-VO2-Max-for-Zwift-and-Strava/
// BLE by Andreas Spiess https://github.com/SensorsIot/Bluetooth-BLE-on-Arduino-IDE
// Modifications by Ulrich Rissel
//
// TTGO T-Display: SDA-Pin21, SCL-Pin22
//+++++++++++++++++++++++++++++++++++++++++++++++++++++++++++++++

/*Board: ESP32 Dev Module
Upload Speed: 921600
CPU Frequency: 240Mhz (WiFi/BT)
Flash Frequency: 80Mhz
Flash Mode: QIO
Flash Size: 4MB (32Mb)
Partition Scheme: Default 4MB with spiffs (1.2MB APP/1.5 SPIFFS)
Core Debug Level: None
PSRAM: Disabled*/

// Set this to the correct printed case venturi diameter
#define DIAMETER 20

#define VERBOSE // additional debug logging

#include <Arduino.h>
#include "esp_adc_cal.h" // ADC calibration data
#include <EEPROM.h>      // include library to read and write settings from flash
#define ADC_EN 14        // ADC_EN is the ADC detection enable port
#define ADC_PIN 34
int vref = 1100;

#include "DFRobot_OxygenSensor.h" //Library for Oxygen sensor
#include "SCD30.h"                //Library for CO2 sensor
#include "Omron_D6FPH.h"          //Library for differential pressure sensor
#include <SPI.h>
#include <TFT_eSPI.h> // Graphics and font library for ST7735 driver chip
#include <Wire.h>
#include "Adafruit_BMP280.h" // Library for BMP280 ambient temp and pressure, set correct I2C address 0x76

// declarations for bluetooth serial --------------
#include "BluetoothSerial.h"
#if !defined(CONFIG_BT_ENABLED) || !defined(CONFIG_BLUEDROID_ENABLED)
#error Bluetooth is not enabled! Please run `make menuconfig` to and enable it
#endif
BluetoothSerial SerialBT;

// declarations for BLE ---------------------
#include <BLE2902.h> // used for notifications 0x2902: Client Characteristic Configuration
#include <BLEDevice.h>
#include <BLEServer.h>
#include <BLEUtils.h>

const String Version = "V2.2 2023/01/23";

byte bpm;

byte heart[8] = {0b00001110, 60, 0, 0, 0, 0, 0, 0}; // defines the BT heartrate characteristic

// Byte[0]: flags: 0b00001110:
// not used/n.u./n.u./RR value available/Energy val.av./
// Sensor contact status/Sens.cont.supported/HR Format: (0: uint_8)
// Byte[1]: HR (uint_8)
// Byte[2]: Energy in J MSB
// Byte[3]: Energy in J LSB
// Byte[4]: RR
// Byte[5]: RR
// Byte[6]: ?
// Byte[7]: ?

byte hrmPos[1] = {2};

bool _BLEClientConnected = false;

// heart rate service
#define heartRateService BLEUUID((uint16_t)0x180D)
BLECharacteristic heartRateMeasurementCharacteristics(BLEUUID((uint16_t)0x2A37), BLECharacteristic::PROPERTY_NOTIFY);
BLECharacteristic sensorPositionCharacteristic(BLEUUID((uint16_t)0x2A38), BLECharacteristic::PROPERTY_READ);
BLEDescriptor heartRateDescriptor(BLEUUID((uint16_t)0x2901));
BLEDescriptor sensorPositionDescriptor(BLEUUID((uint16_t)0x2901)); // 0x2901: Characteristic User Description

class MyServerCallbacks : public BLEServerCallbacks
{
    void onConnect(BLEServer *pServer) { _BLEClientConnected = true; };

    void onDisconnect(BLEServer *pServer) { _BLEClientConnected = false; }
};

// ------------------------------------------

#include <Adafruit_BMP280.h> //Library for barometric sensor
Adafruit_BMP280 bmp;

// Starts Screen for TTGO device
TFT_eSPI tft = TFT_eSPI(); // Invoke library, pins defined in User_Setup.h

// Labels the pressure sensor: mySensor
Omron_D6FPH presSensor;

// Label of oxygen sensor
DFRobot_OxygenSensor Oxygen;
#define COLLECT_NUMBER 10           // collect number, the collection range is 1-100.
#define Oxygen_IICAddress ADDRESS_3 // I2C  label for o2 address

uint8_t data[12], counter; // ??? not used ??? ########################################
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

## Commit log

2023-07-07 Update README - update table.md
    added parts to rest of table, still missing tubing
2023-07-08 button and housing build image
2023-07-09 Update README.md
    update re 16 vs 20mm venturi tube in section "Print 3D parts"
2023-07-11 Update platformio.ini
    commented out
    ;board_upload.maximum_size = 8388608
    ;board_build.partitions = default_8MB.csv
    ;board_build.f_flash = 80000000L
2023-07-11 Update README.md
    updated board description, still not sure I have the right board (don't think this one is touch)
2023-07-11 Update README.md
    updated to correct board, "T" for touch, T-display
2023-07-11 adding wiring image
    From https://www.instructables.com/Real-VO2Max-Measure-Your-Athletic-Potential/
2023-07-12 Update README.md
    add "wipe board", type of board to 16MB 9201F, and use Windows not Mac
2023-07-12 Update platformio.ini
    commented the following back in because I'm using a 16MB board
    board_upload.maximum_size = 8388608
    board_build.partitions = default_16MB.csv
    board_build.f_flash = 80000000L
2023-07-13 add sensor measurement fils
2023-07-13 added sensor measurement image
    sensor measurements
2023-07-13 Update README.md
    added sensor measurement image
2023-07-13 Add files via upload
    added in smaller version of sensor measurements
2023-07-13 Delete sensor_measurements.JPG
    added to wrong folder
2023-07-19 add CFD files for venturi tube design testing
2023-07-19 added mockup of CO2 openings
    Isolates the sensor from pressure fluctuations and we have a wide enough opening for fast readings. Regarding the pressure fluctuations sensitivity, rounded walls around each hole extruded outwards p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
2023-07-23 correctly named and labeled redesigned housing file
2023-07-24 v4 vapor velocity and pressure contours
2023-07-27 pic of first print of v4
2023-08-02 Update README.md
    added o-ring for oxygen sensor to parts list
2023-08-05 adding in v1.0 print files
    Adding v1.0 of the print with mount points for the boards & sensors
    [T0 230802 VO2 Max v1_1.3mf]
2023-08-05 renamed test file folder to test 3d
    [T0 230802 VO2 Max v1_1.3mf]
2023-08-07 Update platformio.ini
    Using BMP280 Libs and sensors
2023-08-07 Update main.cpp
    Update to BMP280 sensors and LIBS
2023-08-07 Update BOM.md
    added jumper wire, noted that 2 items (threaded inserts & aquarium tubing) are no longer needed with new design.
2023-08-09 Update main.cpp
    updated diameter to 20mm
2023-08-12 adding image of print with sensors mounted
    Haven't attached the battery or switch yet.
2023-08-15 changed file names to reflect new version
    [ComputerCover.3mf, MainBody.3mf, MaskAttachment.3mf, SCD30 Cover.3mf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]
2023-08-29 v4.1
    Next iteration of the v4 print.
2023-09-06 added in robert_notes.md
    Robert's notes on finding the project. Maybe we should build a bunch of the sensor options we've explored as a separate list?
2024-12-12 Add module tests
    Start refactoring the code to enable module testing for the device.
    Add tests for PressureSenor and OxygenSensor.
2024-12-12 Add support for Omron D6F-PH5050AD4 sensor
    Add the Dp conversion contants for Omron PH5050AD4.
2024-12-26 Add support for smaller lilygo t-display
    Add suport for the 4MB version of the lilygo t-display.
    Add initial support for barometer and CO2 sensor tests.
2025-01-13 re-anable humidity sensor
    [MaskAttachment.3mf, VenturiSensor.3mf]
2025-07-27 backup lobasl changes
    [SideComputer.3mf, Venturi CO2 20mm.3mf, button.3mf]
2025-10-05 Fixes for SDC30
    - Error detection.
    - Add support for reading the FW version.
    - Read the FW version at initialize to verify the device is working.
2025-12-07 Small fixes for oxygen sensor
2026-01-06 Refactoring volume calculus
    Change the volume calculation to recognize the ventilation state and
    report after exhalation stage.
2026-02-07 Refactor the VO2 BLE server and serial output
    Move VO2 BLE functionality to separate class.
    Refactor the serial output to print a set of json "lines", that can be
    easily parsed.
2026-02-28 Add forced calibration value support for SCD30
